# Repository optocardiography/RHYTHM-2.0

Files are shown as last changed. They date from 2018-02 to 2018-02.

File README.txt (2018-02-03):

RHYTHM 2.0: Panoramic Imaging Toolkit
February 2, 2018

Supported Platforms:
	[1] Mac OS X
	[2] Windows
	[3] Linux

System Requirements:
	[1] MATLAB R2016A or better
	[2] MATLAB compatible C++ compiler (XCode 8.0 for Mac, MinGW 5.3/Visual Studio 2010 or better for Windows, gcc-4.9 for Linux)

Toolkit includes:
	[1] Documentation - contains user manual for MATLAB software, 3D-printed parts list and descriptions, experimental setup parts list
	[2] Resources - contains STL files for 3D-printed parts, manuscript relevant to toolkit
	[3] Source Code - Contains MATLAB files for data analysis, LabView files for geometry acquisition

A sample dataset can be found along with the Github release at https://github.com/optocardiography/RHYTHM-2.0

Please email optocardiography@gmail.com with any questions or concerns, and visit efimovlab.org for more information.

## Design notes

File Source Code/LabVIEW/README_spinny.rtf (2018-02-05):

Spinny

Labview application to drive camera rotator and acquire images.

JMR 6/2014
updated 8/2014
updated 10/2014
updated 01/2015

Rotator Hardware:

The rotator is driven by a stepper motor (17HS16-0284S). The motor connects to a bipolar stepper motor driver (ST-6128) via 4 wires (A+/A-/B+/B-). The setting of the driver: current=0.25, microstep=1 (full step driving mode). An individual 12V/1A DC power supply provides the power to the motor driver. The digital interface of the driver is a standard common anode single pulse interface (optically isolated). The digital (TTL) signals that drive the motor are generated by an arduino microcontroller. The arduino board connects to the driver via a logic invertor (74LS04) for the common anode interface. The plus ends of each signal (PUL+,DIR+,ENA+) are connected to the 5V power on the ardunio board. The PUL-/DIR-/ENA- are 3 digital inputs. PUL- is the step pulse input, falling-edge triggered. DIR- controls the direction, HIGH=CW, LOW=CCW. ENA- is the “Enable” signal, controls the on/off of the motor, active-high. The pulse signal from ardunio pin2 is inverted by 74LS04, connected to PUL-. The direction signal from ardunio pin3 is inverted, connected to DIR-. The Enable signal from ardunio pin4 is non-inverted (inverted twice by 74LS04 to drive the optical isolator), connected to the ENA-. The pin5 on ardunio generates the trigger signal for Dalsa cameras, and connects to a BNC connector which is fixed on the side of the box. The max tested pulse rate at 12V/250mA is 700Hz, for stability, the speed in the Labview is set as 600Hz. There are 416.666 steps per degree, in the labview, a integer of 417 was used, with an negligible error of +0.08%(+0.288° per 360°). The arduino is connected to the computer with a standard USB cable.

Camera Hardware:

The current camera is a Dalsa Genie HM640 8 bit monochrome digital camera. It uses the GigE Vision interface. The camera’s data connection to the computer is a 4-twisted-pair ethernet cable. The computer should have a dedicated intel Pro/1000 NIC in a PCIe slot. There is also a round Hirose connector for power (pins 1 (-) and 2 (+) ) and TTL trigger signal (pins 5 (-) and 6 (+) ). The trigger signal originates from pin 5 on the arduino. Power is 12 VDC at least 600 mA.

Camera Cable:

The cable is 6-twisted-pair (24 gauge) flexible. 4 pairs carry the gigE Vision data. One pair carries the trigger signal, and the last pair carries power (12 VDC at least 600 mA for the camera and another 600 mA for the accessories (electroluminescent backdrop(600mA)/red headlight(400mA)/laser pointer(<20mA)). Because backdrop and headlight do not work at same time, 600mA is enough. Power and trigger go to the hirose connector. A short cable comes out of the back of the hirose for accessories power (red and black pin plug). All accessories have their own power regulator, no additional regulator needed.

Power is in the red(+)/blue(-) pair.

Trigger is in the purple(+)/black(-) pair.

Data is in the remaining pairs. The connectors are RJ45 for Cat6 cable. Looking at the business end of the connector with the tab down, the order of wires is

brown / white
gray-pink striped / pink
gray / red-blue stripe
green / yellow

Arduino Software:

The arduino driver software and IDE must be installed. The software interface between Labview and the arduino is a modified version of LIFA (Labview Interface For Arduino). The labview interface has been modified to implement additional commands for motor/camera control and to generate camera trigger signals at configurable step intervals. Search for “jmr” to see modifications. After plugging in the arduino, but before using the spinny labview application, open LIFA_BaseWithLocalMods in the arduino IDE and download the software to the arduino.

LabVIEW Environment:

NI-IMAQdx is needed for camera communication. This is part of NI Vision Acquisition Software. The LavVIEW interface for arduino (LIFA) toolkit must also be installed. The camera can be configured (e.g., field of view) using the MAX program.

Spinny Usage:

Before starting the VI, select the camera (If a camera is connected it should be visible in the camera pull-down).

When the VI is running, its current position (in degrees) is displayed.

The HOME button sets the position to 0.

On startup, the Camera Mode is “none.” Selecting “live” will play live images in the window. This can be used for aiming and focusing.

To move the camera, select either an angle to move *to* or an angle to move *for* and press the corresponding button. A single camera movement is limited to 360 degrees. To minimize jerking, motor speed will gradually increase from 0 to top speed and also decelerate from top speed to 0 at the end of motion. Maximum speed and acceleration rate are currently hardcoded.

If camera mode is “live” images will continue to be displayed.

When the camera is moving, the only active control is STOP, which will abort the move without losing the current position. However, if the camera has crashed into something solid, it is possible that the stepper motor has lost steps, and the position may not be accurate. In this case, move the arm (using the motor or manual knob) to a physically verifiable 0 position and re-HOME.

If the camera mode is “triggered,” images will be snapped at the specified angular increment. The images will be displayed in the window and also saved to the specified folder. A new folder must be used for each acquisition unless you intend to overwrite. Images in the folder will be sequentially numbered starting from _000 with the same root name as the folder. A text file will be written to the folder that lists the beginning and ending angles of the acquisition, the angular increment, and the direction of rotation. Also, a text file will be generated for each image that indicates the angular position at which the image was saved (which may be slightly different than the angle at which it was acquired). NOTE: an image will be acquired for the starting position and the ending position. Thus, for a 360 degree movement, the first and last images will be from the same position.

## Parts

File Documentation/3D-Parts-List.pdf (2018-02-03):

3D-Printed Parts
Rabbit Tissue Chamber
The tissue chamber was designed to contain a rabbit’s heart as well as the perfusion solution. 8 screws (2 on each side) would situate the chamber to a magnetic table. The 4 big windows were created so the cameras would be able to view the heart as it is in the chamber. The smaller windows allow light to pass through, increasing the visibility of the heart during experimentation. The two holes on the side are for the inflow and outflow of the perfusion system.

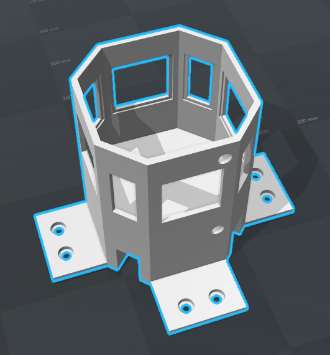
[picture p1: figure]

Mouse Tissue Chamber
This tissue chamber uses a similar design to the rabbit tissue chamber with the 4 big windows and 4 smaller windows. The difference is that the chamber does not secure onto a magnetic table with screws, but is placed on top of an object to be in the same plane as the cameras.

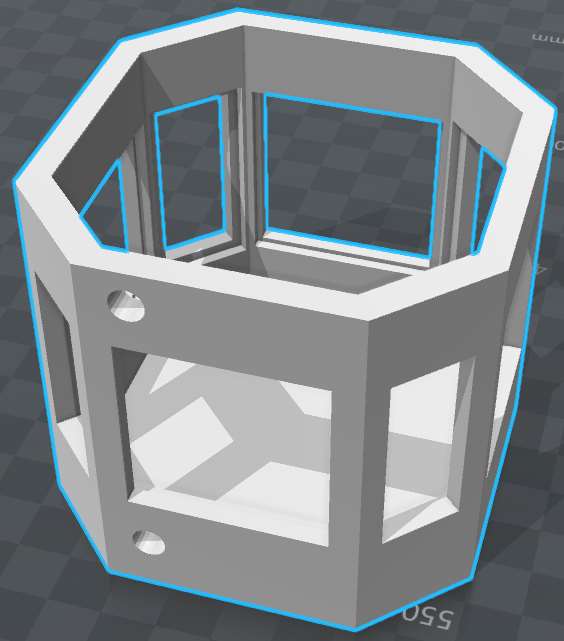
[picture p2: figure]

Bubble Trap Mount
The mount was designed to place a bubble trap on top of the rotation stage to prevent air bubbles from entering the heart through the cannula. The exact height is determined by comparing pressure and flow rate. Long screws would allow this to attach to the top plate of the heart platform, putting the rotation stage in the middle.

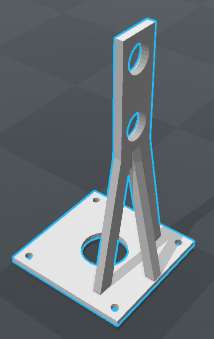
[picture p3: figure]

Cannula Holder
The cannula mount was designed to attach the rotation base to the heart via a cannula. The cannula would be inserted in the center, and the base of the holder would be screwed to the part of the rotation stage that rotates. This allows the heart to rotate as well, useful for geometry acquisition. Ag-AgCl electrodes are inserted in the round holes to record pseudo-ECG, and the wires are passed inside towards the center.

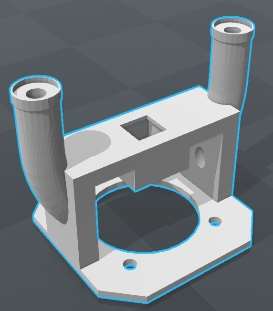
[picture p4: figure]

Top Plate
This plate helps situate the heart platform to prevent movement while in solution. The long screws from the bubble trap mount pass through this plate, and nuts secure it all together. There is a pillar that goes into the slit to attach the platform to this plate.

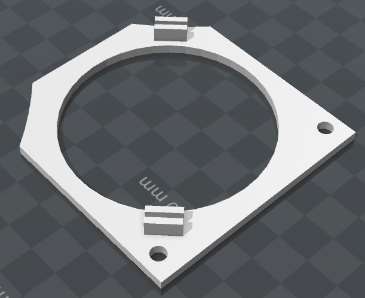
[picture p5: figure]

Pillar
This pillar attaches the top plate to the platform.

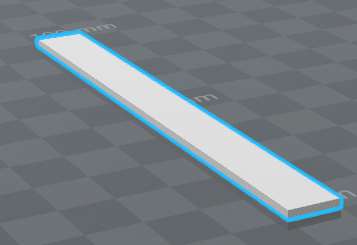
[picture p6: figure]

Heart Platform
This platform is designed to fix the apex of the heart to prevent swaying as it is in the perfusion solution. A suture is passed through the apex and through the hole, brought back around the corner and clipped to the side using a binder clip. The pillar is used to attach the platform to the plate to make it sturdy.

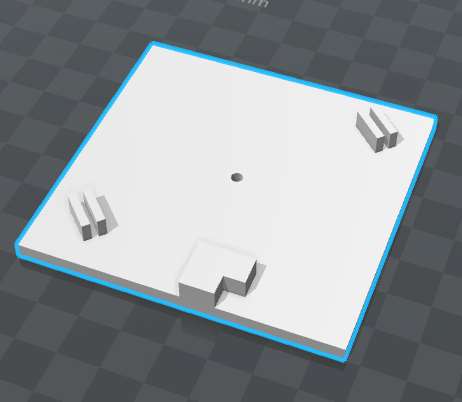
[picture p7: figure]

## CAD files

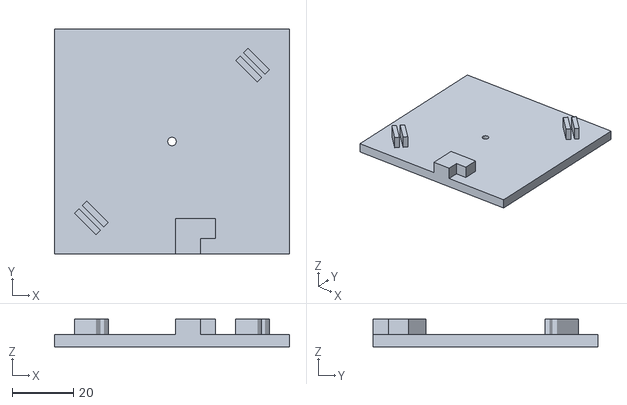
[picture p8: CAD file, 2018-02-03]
Resources/3D-Parts/Platform.stl
76.6 x 73.3 x 9.00

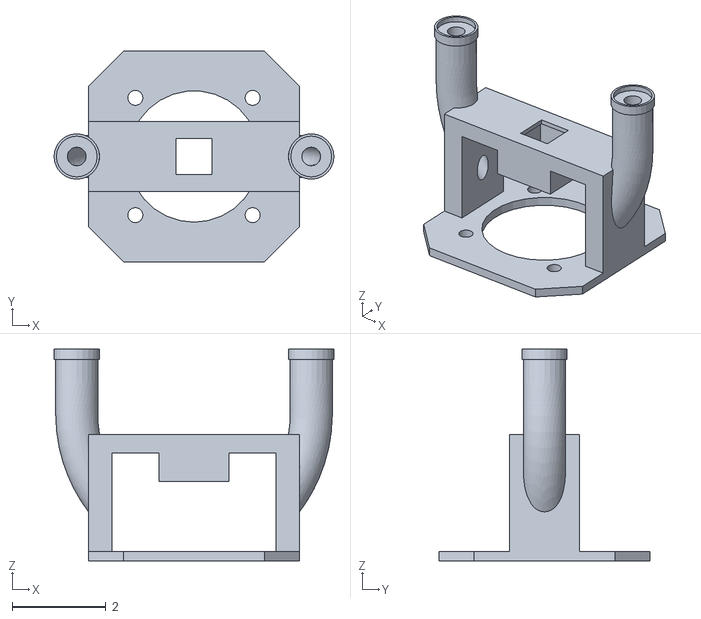
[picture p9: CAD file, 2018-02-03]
Resources/3D-Parts/CannulaHolder.stl
5.97 x 4.50 x 4.52

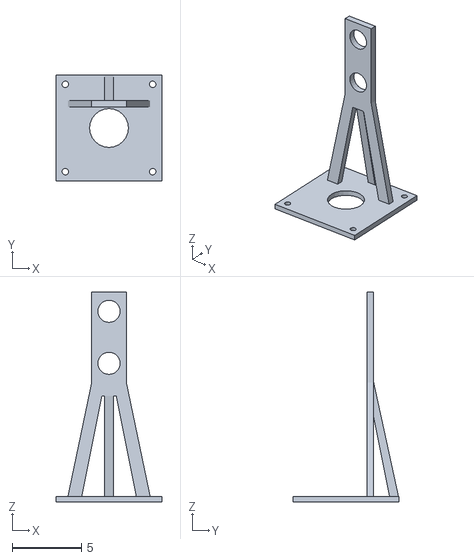
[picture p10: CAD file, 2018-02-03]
Resources/3D-Parts/BubbleTrapHolder.stl
7.66 x 7.66 x 15.1

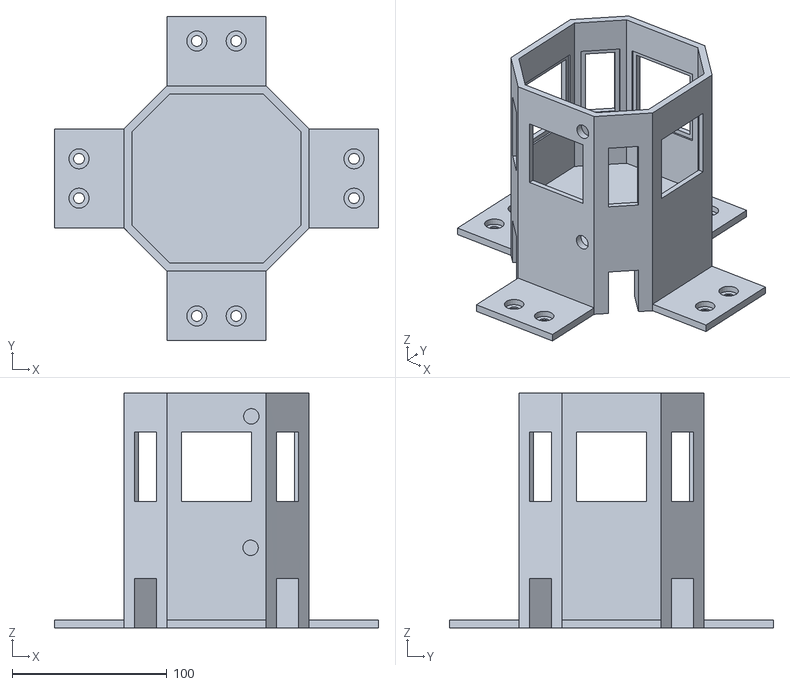
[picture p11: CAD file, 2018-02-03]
Resources/3D-Parts/Rabbit-TissueChamber.stl
209.5 x 209.5 x 151.8

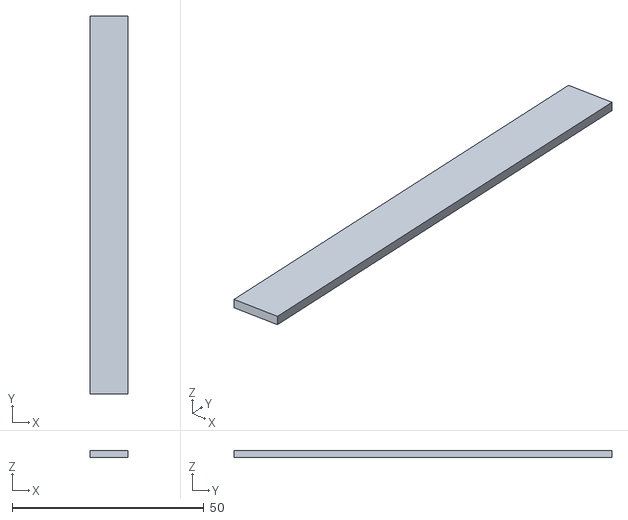
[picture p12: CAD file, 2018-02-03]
Resources/3D-Parts/Pillar.stl
10.00 x 98.5 x 1.75

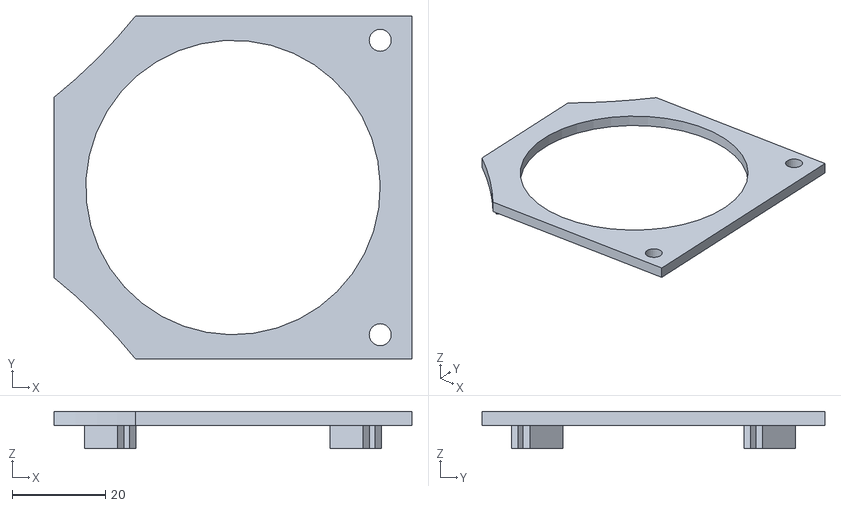
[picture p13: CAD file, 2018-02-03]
Resources/3D-Parts/TopPlate.stl
76.6 x 73.3 x 8.00

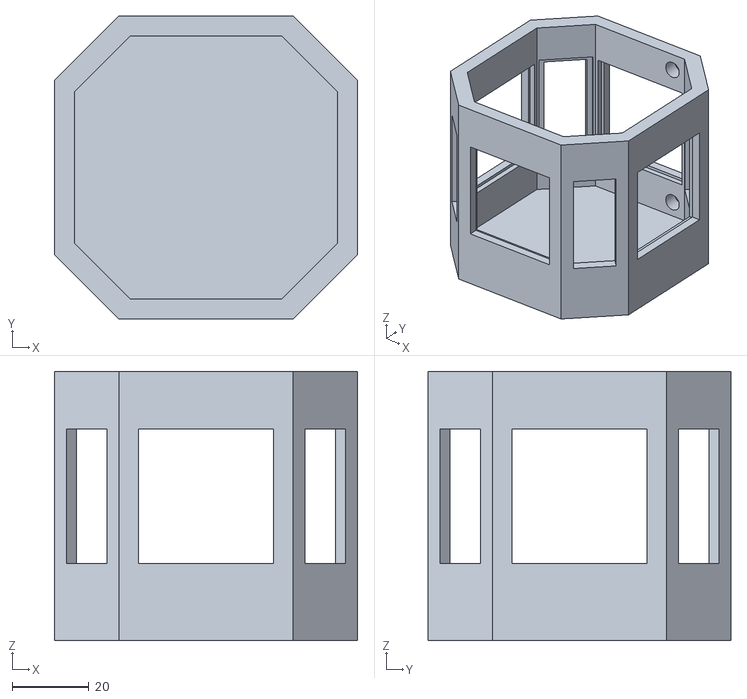
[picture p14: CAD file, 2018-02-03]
Resources/3D-Parts/Mouse-TissueChamber.stl
78.8 x 78.8 x 70.0

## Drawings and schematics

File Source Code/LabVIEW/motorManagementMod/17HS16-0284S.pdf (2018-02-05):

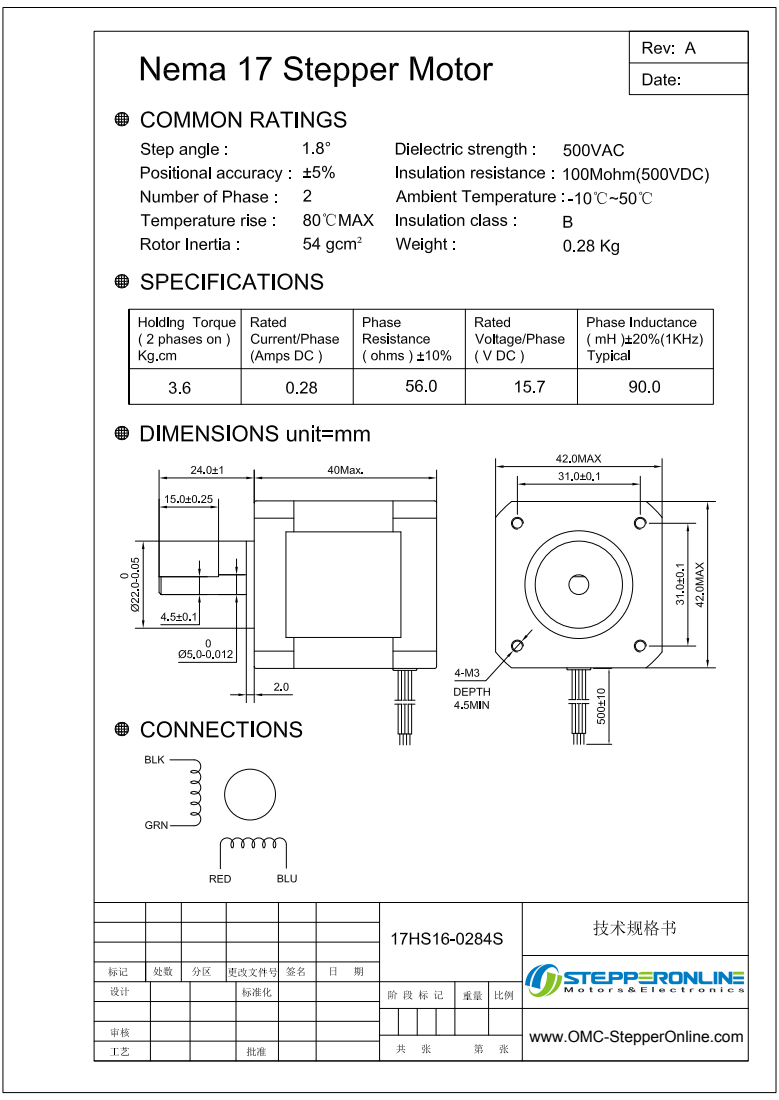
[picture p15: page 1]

www.OMC-StepperOnline.com

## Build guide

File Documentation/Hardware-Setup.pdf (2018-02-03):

Hardware Setup
Camera Setup

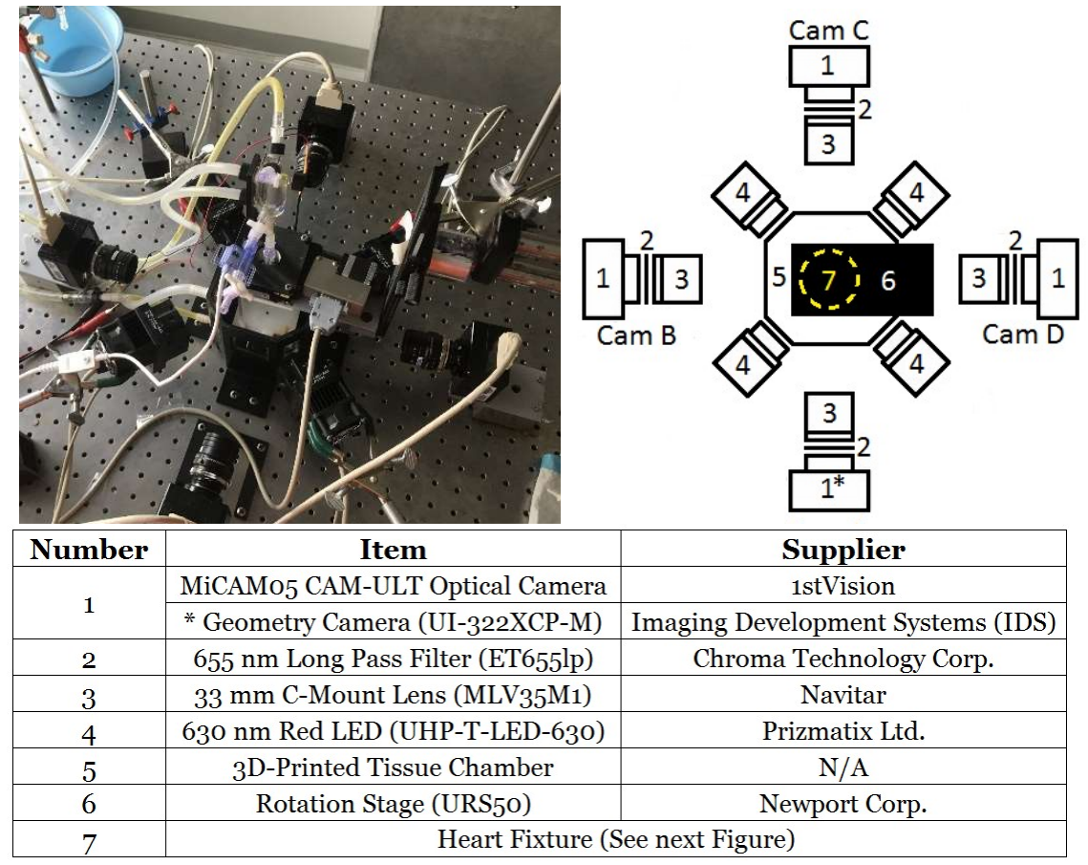
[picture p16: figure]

The camera setup involves 4 cameras located 90 degrees away from each other. Camera 1 can either be the optical camera or the geometry camera, while cameras 2-4 are optical cameras. Each camera has a long pass filter and c-mount lens attached, and is secured to a magnetic table using magnetic stands from ThorLabs and Gaertner Scientific Corporation. Between each camera is a red LED also secured to the table using magnetic stands. A 3D-printed tissue chamber is placed in the center of the setup, with a rotation stage above it. The optical cameras are attached to an acquisition system connected to the computer to save videos and pictures.

Heart Fixture

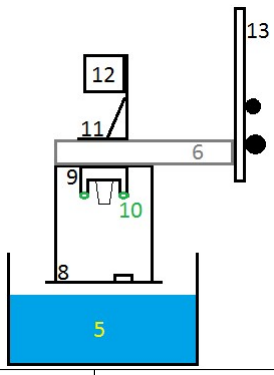
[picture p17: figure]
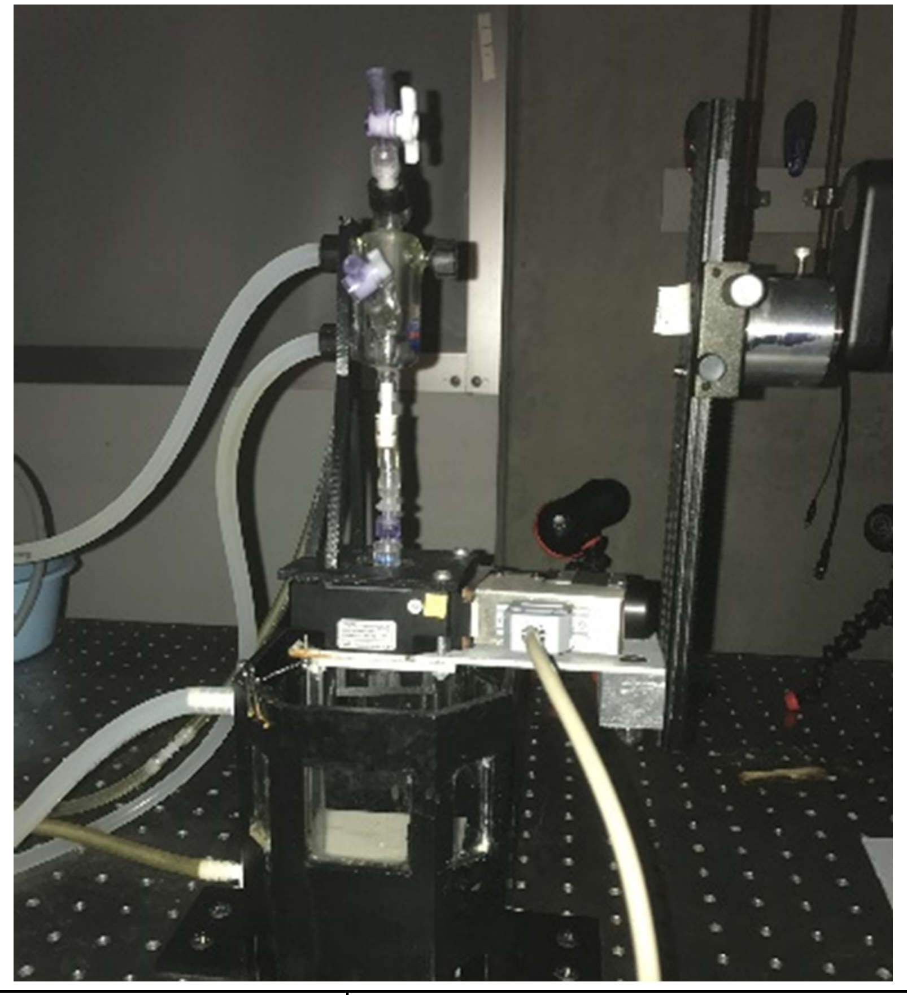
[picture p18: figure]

The heart fixture consists of many 3D-printed parts. The heart platform is used for tying down the apex of the heart to minimize movement of the heart while taking recordings and is attached to the bottom of a platform holding the rotation stage. The platform leveler lowers and raises fixture into/out of the chamber. Attached to the bottom of the rotation stage is a cannula mount designed to hold the cannulated part of the heart. On the ends are Ag-AgCl electrodes used to record pseudo-ECG readings. On top of the rotation stage is a bubble trap mount that attaches the bubble trap at a height. The exact height is determined by comparing the pressure and flow rate. This fixture is attached to a Diagnostic Instruments stand able to raise and move the entire fixture, which is necessary when trying to minimize camera changes for calibration and geometry acquisition. The perfusion system to the chamber consists of MasterFlex tubing connecting multiple bubble traps to two MasterFlex pumps (one for inflow and one for outflow).

Number | Item | Supplier
8 | 3D-Printed Heart Platform | N/A
9 | 3D-Printed Cannula Mount | N/A
10 | Ag-AgCl Electrode | Sigma-Aldrich
11 | 3D-Printed Bubble Trap Mount | N/A
12 | Bubble Trap | Radnoti
13 200mm Movable 2-Way | Focusing Rail Slider | FotoMate

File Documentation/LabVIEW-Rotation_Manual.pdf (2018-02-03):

How To: Rotating Using LabVIEW

Shubham Gupta

Updated September 9, 2017

This manual explains how to use the LabVIEW interface to rotate the heart and acquire images for geometry reconstruction.

Launching the Interface

Before opening the program, be sure that your camera is plugged in and on.

Open LabVIEW and launch SpinnyGloSingle.vi. You should get this window:

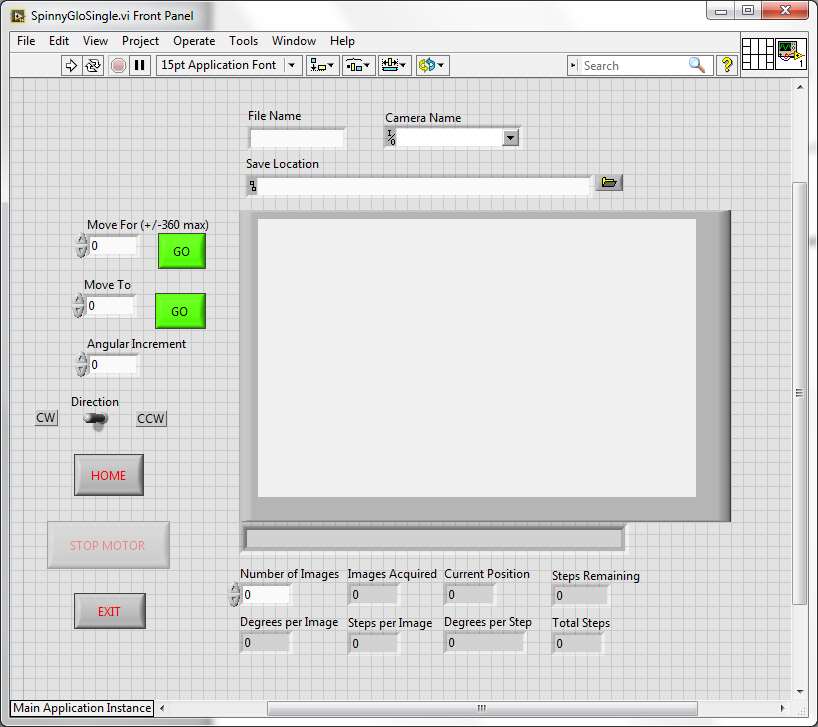
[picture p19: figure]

Setting Initial Parameters

Before you run the program, you need to set the camera name. Use the dropdown to select the camera you are using.

If nothing shows up in the dropdown, be sure that your camera is plugged in and is on. Then reopen the program.

Now run the program by clicking the right arrow at the top.

You should be able to see a live feed of your camera.

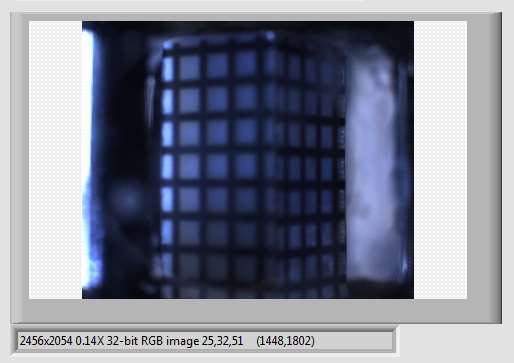
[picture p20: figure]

Disclaimer: The images might be flipped vertically. You can manually flip the images after collection. Select all the flipped images and right-click. Click ‘Rotate Clockwise’. Repeat the process again to do a complete flip.

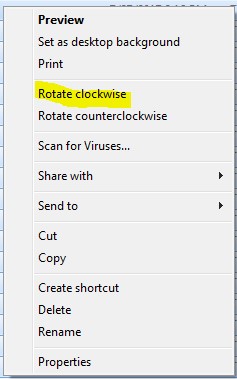
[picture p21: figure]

Type in a file tag in the ‘File Name’ box. The files will be named ‘Your_Tag_Name1.tiff’, ‘Your_Tag_Name2.tiff’, ‘Your_Tag_Name3.tiff’, etc.

Click the folder icon to select the location where you want the images to be saved.

Setting Angles and Number of Images

Set the ‘Move For’ angle to be your starting position. Usually this value is 0. Set the ‘Move To’ angle to be your ending position. To rotate 360°
, set this value to 360.

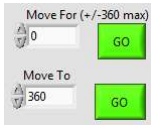
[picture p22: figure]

The ‘Angular Increment’ value determines how often you want images to be taken. For 72 images, we set this value to be 360/72 = 5.

Choose the direction of rotation to be counter-clockwise. You can change the direction by clicking on the pointer.

Type in the number of images you want to collect in the ‘Number of Images’ box. Using a 5

°
step,
this value should be 72.

Starting the Rotation

Once you have inputted all the necessary parameters, hit the bottom ‘GO’ button next to the ‘Move To’ box.

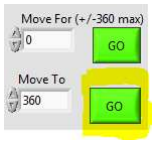
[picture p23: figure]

The bottom boxes will get calculated and stay constant throughout the rotation. The top boxes (except for ‘Number of Images’) will be updated to reflect the progress of the rotation.

Be sure to check the images and ensure that the rotation was successful. If not, make sure nothing is slowing the rotation stage down and try again.

If you have any questions, found any issues, or have new ideas, email sgupta2020@gwu.edu.

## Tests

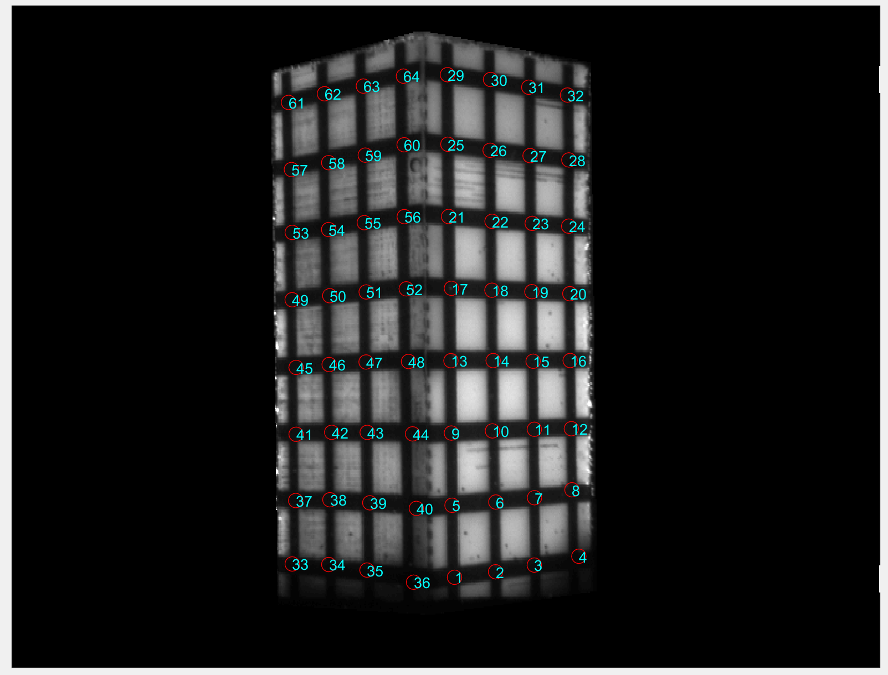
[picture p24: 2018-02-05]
Source Code/MATLAB/FIT_files/fullCalibration.tif

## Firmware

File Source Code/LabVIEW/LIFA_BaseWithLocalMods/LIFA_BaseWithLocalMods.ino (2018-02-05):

/*********************************************************************************
 **
 **  LVFA_Firmware - Provides Basic Arduino Sketch For Interfacing With LabVIEW.
 **
 **  Written By:    Sam Kristoff - National Instruments
 **  Written On:    November 2010
 **  Last Updated:  Dec 2011 - Kevin Fort - National Instruments
 **
 **  This File May Be Modified And Re-Distributed Freely. Original File Content
 **  Written By Sam Kristoff And Available At www.ni.com/arduino.
 **
 
 LOCAL MODS JMR 4/2014
 *********************************************************************************/


/*********************************************************************************
 **
 ** Includes.
 **
 ********************************************************************************/ 
// Standard includes.  These should always be included.
#include <Wire.h>
#include <SPI.h>
#include <Servo.h>
#include "LabVIEWInterface.h" 

/*********************************************************************************
 **  setup()
 **
 **  Initialize the Arduino and setup serial communication.
 **
 **  Input:  None
 **  Output: None
 *********************************************************************************/
void setup()
{  
  // Initialize Serial Port With The Default Baud Rate
  syncLV();

  // Place your custom setup code here
  
  pinMode(2,OUTPUT); digitalWrite(2,LOW);
  pinMode(3,OUTPUT); digitalWrite(3,LOW);
  pinMode(4,OUTPUT); digitalWrite(4,LOW);
  pinMode(5,OUTPUT); digitalWrite(5,LOW);
  pinMode(6,OUTPUT); digitalWrite(6,LOW);
  pinMode(7,OUTPUT); digitalWrite(7,LOW);
  pinMode(8,OUTPUT); digitalWrite(8,LOW);
  pinMode(9,OUTPUT); digitalWrite(9,LOW);
  pinMode(10,OUTPUT); digitalWrite(10,LOW);
  pinMode(11,OUTPUT); digitalWrite(11,LOW);
  pinMode(12,OUTPUT); digitalWrite(12,LOW);
  pinMode(13,OUTPUT); digitalWrite(13,LOW);

}


/*********************************************************************************
 **  loop()
 **
 **  The main loop.  This loop runs continuously on the Arduino.  It 
 **  receives and processes serial commands from LabVIEW.
 **
 **  Input:  None
 **  Output: None
 *********************************************************************************/
void loop()
{   
  // Check for commands from LabVIEW and process them.   
 
  checkForCommand();
  // Place your custom loop code here (this may slow down communication with LabVIEW)
  
  
  if(acqMode==1)
  {
    sampleContinously();
  }

}

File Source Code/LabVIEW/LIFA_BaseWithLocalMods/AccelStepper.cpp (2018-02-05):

// AccelStepper.cpp
//
// Copyright (C) 2009 Mike McCauley
// $Id: AccelStepper.cpp,v 1.4 2011/01/05 01:51:01 mikem Exp $

 #if defined(ARDUINO) && ARDUINO >= 100
  #include "Arduino.h"
  #else
  #include "WProgram.h"
  #endif

#include "AccelStepper.h"

void AccelStepper::moveTo(long absolute)
{
    _targetPos = absolute;
    computeNewSpeed();
}

void AccelStepper::move(long relative)
{
    moveTo(_currentPos + relative);
}

// Implements steps according to the current speed
// You must call this at least once per step
// returns true if a step occurred
boolean AccelStepper::runSpeed()
{
    unsigned long time = micros();

//    if (    (time >= (_lastStepTime + _stepInterval))  // okay if both current time and next step time wrap
//         || ((time < _lastRunTime) && (time > (0xFFFFFFFF-(_lastStepTime+_stepInterval)))) )  // check if only current time has wrapped

//    unsigned long nextStepTime = _lastStepTime + _stepInterval;
//    if (   ((nextStepTime < _lastStepTime) && (time < _lastStepTime) && (time >= nextStepTime))
//	|| ((nextStepTime >= _lastStepTime) && (time >= nextStepTime)))

// TESTING:
//time += (0xffffffff - 10000000);


    // Gymnastics to detect wrapping of either the nextStepTime and/or the current time
    unsigned long nextStepTime = _lastStepTime + _stepInterval;
    if (   ((nextStepTime >= _lastStepTime) && ((time >= nextStepTime) || (time < _lastStepTime)))
	|| ((nextStepTime < _lastStepTime) && ((time >= nextStepTime) && (time < _lastStepTime))))

    {
	if (_speed > 0.0f)
	{
	    // Clockwise
	    _currentPos += 1;
	}
	else if (_speed < 0.0f)
	{
	    // Anticlockwise  
	    _currentPos -= 1;
	}
	step(_currentPos & 0x7); // Bottom 3 bits (same as mod 8, but works with + and - numbers) 

//	_lastRunTime = time;
	_lastStepTime = time;
	return true;
    }
    else
    {
//	_lastRunTime = time;
	return false;
    }
}

long AccelStepper::distanceToGo()
{
    return _targetPos - _currentPos;
}

long AccelStepper::targetPosition()
{
    return _targetPos;
}

long AccelStepper::currentPosition()
{
    return _currentPos;
}

// Useful during initialisations or after initial positioning
void AccelStepper::setCurrentPosition(long position)
{
    _targetPos = _currentPos = position;
    computeNewSpeed(); // Expect speed of 0
}

void AccelStepper::computeNewSpeed()
{
    setSpeed(desiredSpeed());
}

// Work out and return a new speed.
// Subclasses can override if they want
// Implement acceleration, deceleration and max speed
// Negative speed is anticlockwise
// This is called:
//  after each step
//  after user changes:
//   maxSpeed
//   acceleration
//   target position (relative or absolute)
float AccelStepper::desiredSpeed()
{
    float requiredSpeed;
    long distanceTo = distanceToGo();

    // Max possible speed that can still decelerate in the available distance
    // Use speed squared to avoid using sqrt
    if (distanceTo == 0)
	return 0.0f; // We're there
    else if (distanceTo > 0) // Clockwise
	requiredSpeed = (2.0f * distanceTo * _acceleration);
    else  // Anticlockwise
	requiredSpeed = -(2.0f * -distanceTo * _acceleration);

    float sqrSpeed = (_speed * _speed) * ((_speed > 0.0f) ? 1.0f : -1.0f);
    if (requiredSpeed > sqrSpeed)
    {
	if (_speed == _maxSpeed)  // Reduces processor load by avoiding extra calculations below
	{
	    // Maintain max speed
	    requiredSpeed = _maxSpeed;
	}
	else
        {
	    // Need to accelerate in clockwise direction
	    if (_speed == 0.0f)
	        requiredSpeed = sqrt(2.0f * _acceleration);
	    else
	        requiredSpeed = _speed + abs(_acceleration / _speed);
	    if (requiredSpeed > _maxSpeed)
	        requiredSpeed = _maxSpeed;
	}
    }
    else if (requiredSpeed < sqrSpeed)
    {
	if (_speed == -_maxSpeed)  // Reduces processor load by avoiding extra calculations below
	{
	    // Maintain max speed
	    requiredSpeed = -_maxSpeed;
	}
	else
        {
	    // Need to accelerate in clockwise direction
	    if (_speed == 0.0f)
	        requiredSpeed = -sqrt(2.0f * _acceleration);
	    else
	        requiredSpeed = _speed - abs(_acceleration / _speed);
	    if (requiredSpeed < -_maxSpeed)
	        requiredSpeed = -_maxSpeed;
	}
    }
    else // if (requiredSpeed == sqrSpeed)
        requiredSpeed = _speed;

//    Serial.println(requiredSpeed);
    return requiredSpeed;
}

// Run the motor to implement speed and acceleration in order to proceed to the target position
// You must call this at least once per step, preferably in your main loop
// If the motor is in the desired position, the cost is very small
// returns true if we are still running to position
boolean AccelStepper::run()
{
    if (_targetPos == _currentPos)
	return false;
    
    if (runSpeed())
	computeNewSpeed();
    return true;
}

AccelStepper::AccelStepper(uint8_t pins, uint8_t pin1, uint8_t pin2, uint8_t pin3, uint8_t pin4)
{
    _pins = pins;
    _currentPos = 0;
    _targetPos = 0;
    _speed = 0.0;
    _maxSpeed = 1.0;
    _acceleration = 1.0;
    _stepInterval = 0;
//    _lastRunTime = 0;
    _minPulseWidth = 1;
    _lastStepTime = 0;
    _pin1 = pin1;
    _pin2 = pin2;
    _pin3 = pin3;
    _pin4 = pin4;
//_stepInterval = 20000;
//_speed = 50.0;
//_lastRunTime = 0xffffffff - 20000;
//_lastStepTime = 0xffffffff - 20000 - 10000;
    enableOutputs();
}

AccelStepper::AccelStepper(void (*forward)(), void (*backward)())
{
    _pins = 0;
    _currentPos = 0;
    _targetPos = 0;
    _speed = 0.0;
    _maxSpeed = 1.0;
    _acceleration = 1.0;
    _stepInterval = 0;
//    _lastRunTime = 0;
    _minPulseWidth = 1;
    _lastStepTime = 0;
    _pin1 = 0;
    _pin2 = 0;
    _pin3 = 0;
    _pin4 = 0;
    _forward = forward;
    _backward = backward;
}

void AccelStepper::setMaxSpeed(float speed)
{
    _maxSpeed = speed;
    computeNewSpeed();
}

void AccelStepper::setAcceleration(float acceleration)
{
    _acceleration = acceleration;
    computeNewSpeed();
}

void AccelStepper::setSpeed(float speed)
{
    if (speed == _speed)
        return;

    if ((speed > 0.0f) && (speed > _maxSpeed))
        _speed = _maxSpeed;
    else if ((speed < 0.0f) && (speed < -_maxSpeed))
        _speed = -_maxSpeed;
    else
        _speed = speed;

    _stepInterval = abs(1000000.0 / _speed);
}

float AccelStepper::speed()
{
    return _speed;
}

// Subclasses can override
void AccelStepper::step(uint8_t step)
{
    switch (_pins)
    {
        case 0:
            step0();
            break;
	case 1:
	    step1(step);
	    break;
    
	case 2:
	    step2(step);
	    break;
    
	case 4:
	    step4(step);
	    break;  

	case 8:
	    step8(step);
	    break;  
    }
}

// 0 pin step function (ie for functional usage)
void AccelStepper::step0()
{
  if (_speed > 0) {
    _forward();
  } else {
    _backward();
  }
}

// 1 pin step function (ie for stepper drivers)
// This is passed the current step number (0 to 7)
// Subclasses can override
void AccelStepper::step1(uint8_t step)
{
    digitalWrite(_pin2, _speed > 0); // Direction
    // Caution 200ns setup time 
    digitalWrite(_pin1, HIGH);
    // Delay the minimum allowed pulse width
    delayMicroseconds(_minPulseWidth);
    digitalWrite(_pin1, LOW);
}

// 2 pin step function
// This is passed the current step number (0 to 7)
// Subclasses can override
void AccelStepper::step2(uint8_t step)
{
    switch (step & 0x3)
    {
	case 0: /* 01 */
	    digitalWrite(_pin1, LOW);
	    digitalWrite(_pin2, HIGH);
	    break;

	case 1: /* 11 */
	    digitalWrite(_pin1, HIGH);
	    digitalWrite(_pin2, HIGH);
	    break;

	case 2: /* 10 */
	    digitalWrite(_pin1, HIGH);
	    digitalWrite(_pin2, LOW);
	    break;

	case 3: /* 00 */
	    digitalWrite(_pin1, LOW);
	    digitalWrite(_pin2, LOW);
	    break;
    }
}

// 4 pin step function for half stepper
// This is passed the current step number (0 to 7)
// Subclasses can override
void AccelStepper::step4(uint8_t step)
{
    switch (step & 0x3)
    {
	case 0:    // 1010
	    digitalWrite(_pin1, HIGH);
	    digitalWrite(_pin2, LOW);
	    digitalWrite(_pin3, HIGH);
	    digitalWrite(_pin4, LOW);
	    break;

	case 1:    // 0110
	    digitalWrite(_pin1, LOW);
	    digitalWrite(_pin2, HIGH);
	    digitalWrite(_pin3, HIGH);
	    digitalWrite(_pin4, LOW);
	    break;

	case 2:    //0101
	    digitalWrite(_pin1, LOW);
	    digitalWrite(_pin2, HIGH);
	    digitalWrite(_pin3, LOW);
	    digitalWrite(_pin4, HIGH);
	    break;

	case 3:    //1001
	    digitalWrite(_pin1, HIGH);
	    digitalWrite(_pin2, LOW);
	    digitalWrite(_pin3, LOW);
	    digitalWrite(_pin4, HIGH);
	    break;
    }
}


// 4 pin step function
// This is passed the current step number (0 to 3)
// Subclasses can override
void AccelStepper::step8(uint8_t step)
{
    switch (step & 0x7)
    {
	case 0:    // 1000
            digitalWrite(_pin1, HIGH);
            digitalWrite(_pin2, LOW);
            digitalWrite(_pin3, LOW);
            digitalWrite(_pin4, LOW);
            break;
	    
        case 1:    // 1010
            digitalWrite(_pin1, HIGH);
            digitalWrite(_pin2, LOW);
            digitalWrite(_pin3, HIGH);
            digitalWrite(_pin4, LOW);
            break;
	    
	case 2:    // 0010
            digitalWrite(_pin1, LOW);
            digitalWrite(_pin2, LOW);
            digitalWrite(_pin3, HIGH);
            digitalWrite(_pin4, LOW);
            break;
	    
        case 3:    // 0110
            digitalWrite(_pin1, LOW);
            digitalWrite(_pin2, HIGH);
            digitalWrite(_pin3, HIGH);
            digitalWrite(_pin4, LOW);
            break;
	    
	case 4:    // 0100
            digitalWrite(_pin1, LOW);
            digitalWrite(_pin2, HIGH);
            digitalWrite(_pin3, LOW);
            digitalWrite(_pin4, LOW);
            break;
	    
        case 5:    //0101
            digitalWrite(_pin1, LOW);
            digitalWrite(_pin2, HIGH);
            digitalWrite(_pin3, LOW);
            digitalWrite(_pin4, HIGH);
            break;
	    
	case 6:    // 0001
            digitalWrite(_pin1, LOW);
            digitalWrite(_pin2, LOW);
            digitalWrite(_pin3, LOW);
            digitalWrite(_pin4, HIGH);
            break;
	    
        case 7:    //1001
            digitalWrite(_pin1, HIGH);
            digitalWrite(_pin2, LOW);
            digitalWrite(_pin3, LOW);
            digitalWrite(_pin4, HIGH);
            break;
    }
}
    
// Prevents power consumption on the outputs
void    AccelStepper::disableOutputs()
{   
    if (! _pins) return;

    digitalWrite(_pin1, LOW);
    digitalWrite(_pin2, LOW);
    if (_pins == 4 || _pins == 8)
    {
	digitalWrite(_pin3, LOW);
	digitalWrite(_pin4, LOW);
    }
}

void    AccelStepper::enableOutputs()
{
    if (! _pins) return;

    pinMode(_pin1, OUTPUT);
    pinMode(_pin2, OUTPUT);
    if (_pins == 4 || _pins == 8)
    {
	pinMode(_pin3, OUTPUT);
	pinMode(_pin4, OUTPUT);
    }
}

void AccelStepper::setMinPulseWidth(unsigned int minWidth)
{
  _minPulseWidth = minWidth;
}

// Blocks until the target position is reached
void AccelStepper::runToPosition()
{
    while (run())
	;
}

boolean AccelStepper::runSpeedToPosition()
{
    return _targetPos!=_currentPos ? runSpeed() : false;
}

// Blocks until the new target position is reached
void AccelStepper::runToNewPosition(long position)
{
    moveTo(position);
    runToPosition();
}
